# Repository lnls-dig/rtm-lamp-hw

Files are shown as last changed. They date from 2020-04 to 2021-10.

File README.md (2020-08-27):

# FOFB Linear Amplifier Board

The Fast Orbit Feedback (FOFB) Linear Amplifier board is a fast current power source designed to drive the corrector magnets distributed through the storage ring. It is part of the Fast Orbit Correction system for the brazilian 4th generation synchrotron light source (Sirius). It consists of a MicroTCA Rear Transition Module (RTM) capable of driving up to 12 current channels synchronously and delivering up to 1A per channel.

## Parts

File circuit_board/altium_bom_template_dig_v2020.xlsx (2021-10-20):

Grupo de Controles Avançados - GCA - LNLS Tel: (19) 3518-2571
BILL OF MATERIALS
Project: |  | Field=ProjectFileName |  |  |  | Rev: | Field=Revision |  | Variant: | Field=VariantName |  |  |  |  | Date: | Field=ReportDate
Column=Mounted | Column=Designator | Column=Part Number | Column=Description | Column=Value | Column=Tolerance | Column=Voltage | Column=Power | Column=TC | Column=Manufacturer | Column=Manufacturer Part Number | Column=Manufacturer1 Example | Column=Manufacturer1 Part Number | Column=PackageDescription | Column=PressFit | Column=SMD | Column=Socket | Column=Quantity | Notes

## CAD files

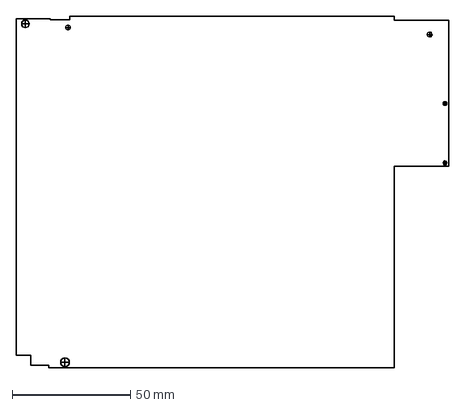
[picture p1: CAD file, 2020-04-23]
mechanical/urtm-outline.dxf
182.5 x 148.5 mm

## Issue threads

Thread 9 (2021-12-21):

### ISSUE TITLE
Driving the DAC output from high to low causes interference in the current measurement

### ISSUE THREAD

**Issue by augustofg** [lnls-dig/rtm-lamp-hw#9]
Channels 0, 2, 3, 5, 6, 8 and 9 are picking up interference from the DAC in the current measurement circuitry. Only when the DAC output swings from 4V to 0V the interference occurs suggesting it might be a grounding issue.

![ch00_dac_interf](https://user-images.githubusercontent.com/8903198/122448997-c0f2d980-cf7b-11eb-9755-db96dbc72637.png)

**Comment by danielot** [comment]
Note: these measurements were taken when opamps were disabled/powered off.

**Comment by augustofg** [comment]
Removing R83 and soldering a 33 ohms resistor directly to the positive and negative inputs of the AD8429 (IC29) makes the glitch to disappear from the input, but the output still behaving the same. One thing I observed it that the positive and negative power supplies, when measuring directly from the inamp pins, show a large voltage glitch (1 - 2Vpp) that might explain this issue:

![inamp_supply_interf](https://user-images.githubusercontent.com/8903198/122786456-b6418880-d28a-11eb-8390-2dda5968f96b.png)

Unfortunately, I couldn't reproduce this in spice, but maybe the [model](https://www.analog.com/media/en/simulation-models/spice-models/ad8429.cir) is not accurate enough.

[rtm-lamp-ad8429-simu.zip](https://github.com/lnls-dig/rtm-lamp-hw/files/6688372/rtm-lamp-ad8429-simu.zip)

**Comment by danielot** [comment]
Do these glitches on the +/-7V power supply happen for positive DAC steps too? It would be nice to see the curves for the positive step as well.

**Comment by augustofg** [comment]
@danielot They do, but at a lower amplitude.

**Comment by augustofg** [comment]
~OK now it seems I'm getting somewhere. Maybe my first attempt to solder an 33 ohms resistor directly into the AD8429 differential inputs wan't making good contact. I've re-soldered it and the glitch is almost gone in channel 8:~

![ch8_dac_interf_shunt_removed](https://user-images.githubusercontent.com/8903198/124326148-5be2da80-db5c-11eb-843c-e1cfc4e04415.png)

I'll try this for the other channels just to be sure.

**Comment by augustofg** [comment]
My mistake, the AD8429 from channel 8 was not powered (I removed the ferrite beads from the AD8429 to test if the disturbances in the +-7V supplies were conducted or irradiated). Here there are the same measurements for channel 5 with the shunt resistor removed and a 30 ohms resistor soldered directly to the inamp differential inpunts:
![ch5_dac_interf_shunt_removed](https://user-images.githubusercontent.com/8903198/124474753-4990b880-dd77-11eb-9280-2679702b23ec.png)

**Comment by augustofg** [comment]
It is a grounding issue. After soldering wires to reduce the ground impedance for C85, C84, C88 and C89 I was able to reduce the glitch amplitude significantly:
![ch5_gnd_fix2](https://user-images.githubusercontent.com/8903198/124983132-fbe1ad80-e00d-11eb-9266-c17521eb0d3a.png)

Fix 1:
![ch5_gnd_top_fix1](https://user-images.githubusercontent.com/8903198/124983597-8cb88900-e00e-11eb-957f-93e193ad3ad1.jpg)

Fix 2:
![ch5_gnd_top_fix2](https://user-images.githubusercontent.com/8903198/124983603-8de9b600-e00e-11eb-94ad-520c9c3af846.jpg)

**Comment by augustofg** [comment]
Solved in the newer releases.

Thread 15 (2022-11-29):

### ISSUE TITLE
Altium files. Save as ASCII

### ISSUE THREAD

**Issue by colin-ab** [lnls-dig/rtm-lamp-hw#15]
Can the be saved as ASCII files so they can be imported into other eCAD software packages?

**Comment by augustofg** [comment]
Hi @colin-ab . I've converted the PCB and schematic files to ascii and put them on a new branch. Please check the [altium-ascii-conv](https://github.com/lnls-dig/rtm-lamp-hw/tree/altium-ascii-conv) branch.

**Comment by colin-ab** [comment]
Many thanks. That's great. Colin-ab @ Diamond Light Source

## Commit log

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2020-04-24 Fix grid spacing [sch]
    The grid in schematic sheets should be set to imperial units (50mil) to
    keep component symbols properly aligned.
    [connectors.SchDoc, management-i2c.SchDoc, power.SchDoc, rtm-top.SchDoc]
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2020-06-10 Extra shift registers [sch]
    Expand the shift registers chain to accomodate 4 extra channels. Also
    replace all 100nF 0805 capacitors to 0603.
    [rtm-top.SchDoc, shift-registers.SchDoc]
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2020-06-16 Replace 2k resistor by 2x 1k resistors [sch]
    Optimize the BOM by replacing a 2k resistor by 2x 1k resistors.
    [power.SchDoc]
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2020-06-19 Bypass the JTAG chain [sch]
    This RTM board doesn't need a JTAG interface.
    [connectors.SchDoc, rtm-lamp.PrjPcb, rtm-top.SchDoc]
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2020-06-26 Fix ERC errors [sch]
    The project still have a lot of warnings that should be addressed.
    [adc.SchDoc, connectors.SchDoc, management-i2c.SchDoc, power-amplifiers.SchDoc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]
2020-06-26 Fix RTM_LVD signals order, ignore multiple net names warning [sch]
    The RTM_LVDx_P and RTM_LVDx_N differential pairs were swaped before
    entering the ADC_LVDS harness in the connectors.SchDoc sheet.
    Unfortunatelly there seems to be no way to proper deal with multiple net
    names in multiple channels hierarchical design, so I turned off the
    multiple net names warning.
    [connectors.SchDoc, management-i2c.SchDoc, power.SchDoc, rtm-lamp.PrjPcb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]
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2020-07-02 Re-enumerate the power-amplifiers sheet, fix channel class [sch pcb]
    Channels 8-11 had a different channel class for some motive. The only
    way to fix it was to delete all channels from schematics, import the
    netlist to the pcb, add all channels to the schematics and import the
    netlist again.
    [power-amplifiers.SchDoc, rtm-top.SchDoc]
2020-07-06 Replace shift registers ICs for smaller footprint versions [sch]
    [connectors.SchDoc, rtm-lamp.PrjPcb, rtm-top.SchDoc, shift-registers.SchDoc]
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2020-07-14 Match the input shift-registers supply with power amplifiers [sch]
    To avoid voltage level problems between the power amplifiers and the
    74HC165 shift registers, both are powered by the same supply now.
    [connectors.SchDoc, rtm-top.SchDoc, shift-registers.SchDoc]
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2020-07-17 Improvements to the voltage level translators [sch]
    - Use ferrite beads to attenuate noise generated by the voltage
    translators;
    - Put resistors in the voltage translators outputs to limit the slew
    rate to limit EMI;
    - Allow DAC_LDAC and ADC_CNV signals to be independly controlled by the
    FPGA;
    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
    [clock-distribution.SchDoc, rtm-connectors.SchDoc, rtm-lamp.PrjPcb, rtm-top.SchDoc]
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2020-07-17 Replace all 0603 resistors with 0402 equivalents [sch pcb]
    [adc.SchDoc, clock-distribution.SchDoc, management-i2c.SchDoc, power-amplifiers.SchDoc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]
2020-07-17 Replace most 0603 capacitors for 0402 equivalents [sch pcb]
    Ceramic capacitors of 100nF or less connected to voltage rails of 5V or
    less were replaced for 0402 equivalents to save PCB space.
    [adc.SchDoc, clock-distribution.SchDoc, management-i2c.SchDoc, power-amplifiers.SchDoc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]
2020-07-17 Replace 1uF tantalum capacitors for MLCs [sch pcb]
    [adc.SchDoc]
2020-07-22 Replace some 0603 capacitors / resistors left for 0402 [sch]
    [power.SchDoc]
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2020-07-28 Fix swaped I2C SCL/SDA signals in IC1, IC13 and IC14 [sch]
    [management-i2c.SchDoc]
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2020-07-30 Replace R59 and R60 for 10k resistors [sch]
    Use 10k resistors instead 36k to improve the available current margin
    for DAC_REF1 and DAC_REF2.
    [power.SchDoc]
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2020-08-04 Improvements in output stability for -7V and +7V supplys [sch]
    Replace C70 and C53 for 10uF capacitors, place after the respective
    ferrite beads. This improves the voutage output ripple under transients
    and gurarantees the minimum ESR necessary for loop stability (LM2991 and
    LM2941).
    [power.SchDoc]
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2020-08-07 Swap GND and +12_EXT signals in J6 to aid routing [sch]
    [power.SchDoc]
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2020-08-10 Swap CH3_L and CH3_H in J4 to the correct order [sch]
    [output-connectors.SchDoc]
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2020-08-12 ADC wrong channel numbering [sch]
    The netlabel for the quad-channel ADC (IC39) should start from AIN9_x.
    AIN8_x is already used by the octo-channel ADC (IC38).
    [adc.SchDoc]
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2020-08-18 Fully routed board [pcb]
    All nets have been routed. Time to deal with the DRC errors.
    [rtm-lamp.PrjPcb]
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2020-09-04 Replace LTC232xIUKG-16 ADCs with LTC232xCUKG-16 [sch pcb]
    The CUKG version is available is in stock on DigiKey. The only
    difference between IUKG and CUKG is the temperature range of operation
    (-40C to +85C vs 0C to +70C respectively).
    [adc.SchDoc, rtm-lamp.PrjPcb]
2020-09-04 Replace SML-311UTT86K with HSMC-C190 [sch pcb]
    The SML-311UTT86K red smd LED seems to be EOL, replace it with the
    HSMC-C190 LED.
    [management-i2c.SchDoc]
2020-09-04 Replace SRN5040TA-4R7M with SRN5040TA-6R8M [sch pcb]
    The SRN5040TA-4R7M seems is not available from major distributors right
    now, replace it with SRN5040TA-6R8M. From my simulations it should work
    fine, the power supply noise is greater than before but still aceptable.
    [power.SchDoc]
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2020-10-15 Move the 220pF capacitors (C87_CHx) near the ADCs [sch pcb]
    Placing the 220pF capacitors far from the ADC would reduce its noise
    attenuation potential.
    [adc.SchDoc, power-amplifiers.SchDoc]
2020-10-16 Replace C86 with a 47nF C0G 0805 ceramic capacitor [sch pcb]
    Although physically larger, it is much more stable with temperature
    variations and the capacitance isn't affected by DC bias.
    [power-amplifiers.SchDoc, rtm-lamp.PrjPcb]
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2020-11-06 Variants fixes [pcb]
    - For some motive R1, R2 and C54 were marked as 'not fitted' on some
    variants, mark as fitted;
    - Always fit J6 for now, even on internal power variants. Use F3 and F2
    to select between external and internal power;
    - Copy all 'not fitted' components from 'INT PWR AFC3.1' to 'INT PWR
    AFC3.1 8 CH'.
    [power.SchDoc, rtm-lamp.PrjPcb]
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2021-02-08 Replace the NJM11100F1 LDO with TPS7A2401 [sch pcb]
    NJM11100F1 seems to have stock problems on the majors distributors.
    Replace it with the Texas TPS7A2401 (IC24 and IC25).
    [power.SchDoc, rtm-lamp.PrjPcb]
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2021-02-08 Fix wrong voltage output from the +3.3V power supply [sch pcb]
    R72 should be swaped with R75 and R138 to IC24 output +3.3V.
    [power.SchDoc]
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2021-02-11 Fix hotswap handle mounting hole position [pcb]
    Commit 749067025277454774fa1e5bc939a1e08d5c16fa moved the hotswap
    mounting hole to an incorrect position.
    [rtm-lamp.PrjPcb]
2021-02-19 Correct I2C address of the CDCE906PW PLL [sch]
    Also update the I2C addresses table to include hexadecimal notation.
    [management-i2c.SchDoc]
2021-02-23 Add a series resistor before ADP1850 VIN [sch pcb]
    The ADP1850's datasheet recommends that a small resistor should be added
    before VIN and decoupling caps to aid noise filtering (RC filter).
    [power.SchDoc]
2021-03-16 Add 10uF ceramic capacitors to +12V_HP, +VS1 and +VS2 rails
    Add 10uF ceramic capacitors to power rails in order to minimize
    switching noise and provide a low impedance source for the power
    transistors T1 and T2.
    [power.SchDoc]
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2021-05-10 Set the OPA569 output current limit to 1.1A [sch pcb]
    Fixes #8
    [power-amplifiers.SchDoc]
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2021-07-15 Invert ADC differential inputs to make things consistent [sch pcb]
    Fix #3
    [adc.SchDoc]
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2021-08-27 Fix the voltage for VS1, VS2, DAC_REF1 and DAC_REF2 to 3.7V [sch pcb]
    Remove trimpots P1, P2, P3 and P4 and fix the voltage to 3.7V for the
    DAC references and power amplifiers supply. This is the maximum voltage
    possible assuming 8 channels sourceing 1A that fits the 36W power
    envelope.
    See #10
    [power.SchDoc]
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2021-08-31 Replace J4 with two 8 pins connectors (like J5) [sch pcb]
    The Molex 3.5mm 16 pins Euroblock connector requires a lot of force do
    separate the male and female parts. Using 2x 8 pin connectors makes it
    much more easy.
    Fixes #12
    [output-connectors.SchDoc]
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2021-09-01 Change loop compensator design for better stability [sch pcb]
    Using the values calculated using the ADP1850's datasheet design
    guide for C22/C32, C23/C36 and R47/R54 results in very low capacitances
    and high resistance values that in turn make VS1_COMP and VS2_COMP
    succeptible to noise resulting in a unstable output (see #2).
    Using a scale factor of 10 for the capacitors and 1/10 for the
    resistors makes VS1 and VS2 much more stable at the cost of a slower
    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
    [power.SchDoc]
2021-09-03 Add status LEDs for power rails [sch pcb]
    Now every power rail has an LED to indicate if it is powered.
    Swap DAC_REF1 and DAC_REF2 IC18 opamp assignment to optimize routing and
    avoid net crosses.
    Closes #11
    [management-i2c.SchDoc, power.SchDoc]
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
